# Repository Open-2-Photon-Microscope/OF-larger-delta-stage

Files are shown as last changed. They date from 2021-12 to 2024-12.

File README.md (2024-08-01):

# Substage Sample Manipulator

---
### A substitute for a micromanipulator

Our design is a modification of [Open Flexure's Delta Stage model](https://openflexure.org/projects/deltastage/) combined with a 3-axis controller box. 
The delta stage is a reliable and useful way of manipulating a small sample in X, Y and Z axes without having to move the optics of the microscope, as most current setups do.

Our aim is to use it to replace expensive hardware like [Sutter's MP-285](https://www.sutter.com/MICROMANIPULATION/mp285_frame.html), which costs a lot and effectively has to hold and manipulate the entire microscope in midair.
The setup we detail is applicable to small, low-weight samples. 
    _For larger animals such as mice, we encourage further exploration and experimentation in other projects elsewhere (but we would love know what you find before we delve in to it ourselves!!)._

This part of the project consists of two main pieces:
1. The delta stage itself, to hold and move the sample
1. [The 3-axis controller](https://github.com/Open-2-Photon-Microscope/3-axis-controller/tree/main), which uses rotary encoders to manually adjust the stage position, without the need to interface with a computer (although entirely possible).

We have made modifications to OpenFlexure's original design to allow compatability with a thorlabs cage-based substage light-collection path you can find elsewhere in the Open-2-Photon-Microscope GitHub.
Since we adjusted the scale and a few other things in the design, and since the release paper does not provide data, we have been testing the delta stage's movement, measuring how reliably it makes the same movements in a given direction, and how robust it is to drift over time. These data can be found in the 'Movement Metrics Data' folder.

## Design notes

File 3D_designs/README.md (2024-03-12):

# 3D Designs

## Optics
 - 3D printable thorlabs-compatible holders for lenses / mirrors

## STL
 - All current stl files for 3D printing:
### Centering:
1. centering card - a flat sheet with a raised hole. Slots over thorlabs cage parts held to Delta Stage. Used in conjucntion with centering top stage.
2. centering top stage - interchangable top stage with a hole for aligning with centering card

### Delta Stage for 2P
- Current working version of the Delta Stage
- large enough to contain thorlabs cage and lens (d=2in)

### Spirit Level
- Essential stage top for attaching a spirit level [url]

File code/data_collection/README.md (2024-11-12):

# Image Capture Protocol for XY Drift Analysis:

The files in this folder pertain to using a USB microscope with the [3-axis controller]() and [OF-larger delta stage](https://github.com/Open-2-Photon-Microscope/OF-larger-delta-stage)In the [`/code/`](https://github.com/Open-2-Photon-Microscope/OF-larger-delta-stage/tree/main/code) folder is a pipeline for analysing .tiff files that are derived from 2-photon microscopy files, however modified versions are named with the prefix 'jpeg' since the images they deal with (still tiff format) originate as jpeg files from the microscope. These files are the ones that will be used below but are dependent on other files in the folder. The protocol they use pertains only to X and Y drift.

## Collecting the Data  

The requires an up-to-date model of the 3-axis controller, and a way of holding the microscope above the sample (anything with distinct features so that movement can be measured).  

1. Download the files from this [folder](https://github.com/Open-2-Photon-Microscope/OF-larger-delta-stage/tree/main/code/data_collection)
2. Ensure the sample is visible from the camera (e.g. with cheese)
3. Ensure the stage is at `[0, 0, 0]` 
4. Running collect_data.py will prompt user to select the folder into which `/drift_data_x/` and all images will be saved (where x is the number of of the iteration)
	1. _NB: This is currently not true, I designed this to get the job done on my computer and it doesn't yet generalise so nicely_
5. The user is then prompted to input the number of iterations. 
	- Each iteration will take images at 9 positions (a 3x3 grid  from `[-4500,-4500]` to `[4500, 4500]`). Images will be taken at 10-minute intervals for two hours (for a total of 13 images including T0).
	- Each iteration creates its own folder
	- The number and length of the intervals the images are taken in may be modified to suit users needs'
	- Choosing many iterations allows autonomous data collection that may run for days

## When it ends  

Once the script is finished running, it will have created many folders. I recommend moving these folders to their own single folder with a clear label and date before running the script again, which would otherwise overwrite them.

## Troubleshooting  

Sometimes trouble happens: _c'est la vie_.  

- The most common error that might happen is:
	`[ WARN:0@3839.300] global cap_v4l.cpp:889 requestBuffers VIDEOIO(V4L2:/dev/video0): failed VIDIOC_REQBUFS: errno=19 (No such device)`  
	At this point the script _should_ automatically stop.
	- __Solution__: 
		1. Unplug and replug the usb microscope
		2. If the terminal is still active run `usb.moveto([0,0,0])` otherwise you will need to re-home the device manually
		3. All iterations / counting will start from 0 again so make sure to move or rename collected data so it is not overwritten

 - Sometimes an error will be in relation to the microcontroller.
	 - __Solution__: 
		 1. close all other programs that relate to the controller (including exit() from the script execution)
		 2. if that doesn't work, try unplugging the controller and turning off the power and plugging it back in (make sure to cross your fingers for good luck)

---
# Analysis Protocol:

#TODO: update this part of the protocol

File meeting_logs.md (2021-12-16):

# Meeting logs (development chat)

### 16/12/2021

Andre and Filip:

Next steps:
- setup full Open Flexure Software environment
 - Sangaboard + RPi
- Check how well it plays with [ScanImage](https://docs.scanimage.org/)
- Figure out a way to control it manually (manipulator or joystick)
- Eventually check if this also works with other software

- research open source manipulators/joysticks to control the substage system
 - if there is nothing available create something.

- find an analogue voltmeter (possible good candidate https://uk.rs-online.com/web/p/multimeters/8105526)

Outcomes from previous work package:
- Open flexure positioning is stable for our application.
- We used Serial commands over the Arduino IDE to quickly check things.

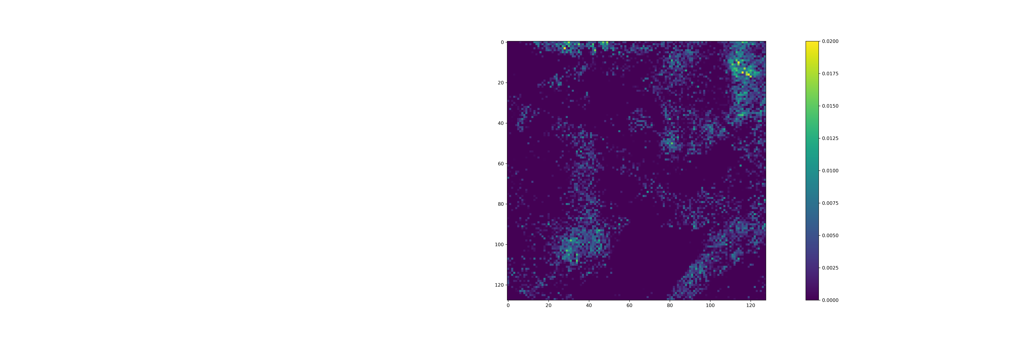
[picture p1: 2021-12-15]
media/between_recording.png

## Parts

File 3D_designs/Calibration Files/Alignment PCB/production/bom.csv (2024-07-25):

Designator | Footprint | Quantity | Value | LCSC Part #
D1, D2, D3, D4 | LED_D3.0mm | 4 | LED 2V 20mA
J1 | JST_XH_B2B-XH-A_1x02_P2.50mm_Vertical | 1 | Conn_01x02_Socket
R1, R2 | R_Axial_DIN0207_L6.3mm_D2.5mm_P7.62mm_Horizontal | 2 | 51

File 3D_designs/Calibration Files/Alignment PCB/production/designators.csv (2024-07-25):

D1:1
D2:1
D3:1
D4:1
J1:1
R1:1
R2:1

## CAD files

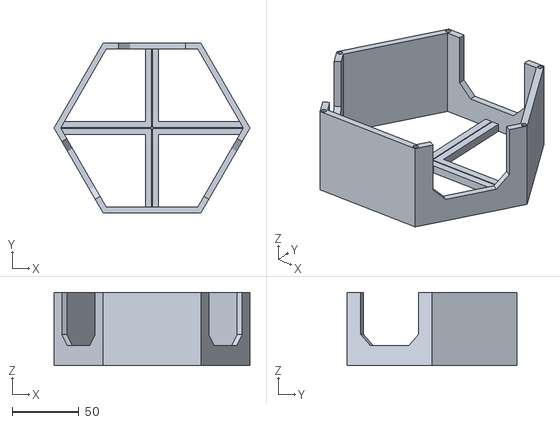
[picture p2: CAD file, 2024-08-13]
3D_designs/Calibration Files/stage_calibration_0_5.stl
147.0 x 127.3 x 55.0

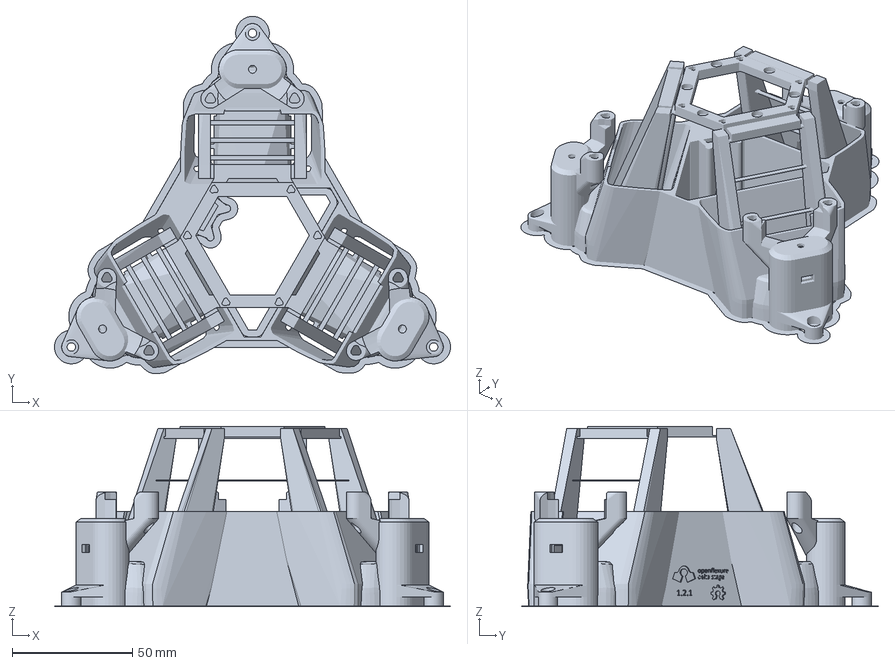
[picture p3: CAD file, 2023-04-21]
3D_designs/delta_stage_with_stage_mount_holes.3mf
164.7 x 148.5 x 75.0 mm

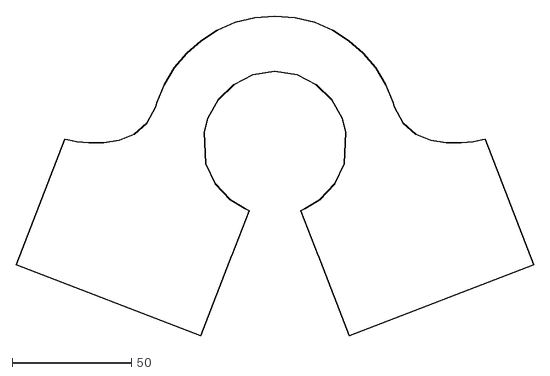
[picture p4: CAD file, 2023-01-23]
3D_designs/open_flexure_delta_copy_20230123/openflexure-microscope/openscad/openflexure_emblem.dxf
216.7 x 134.0

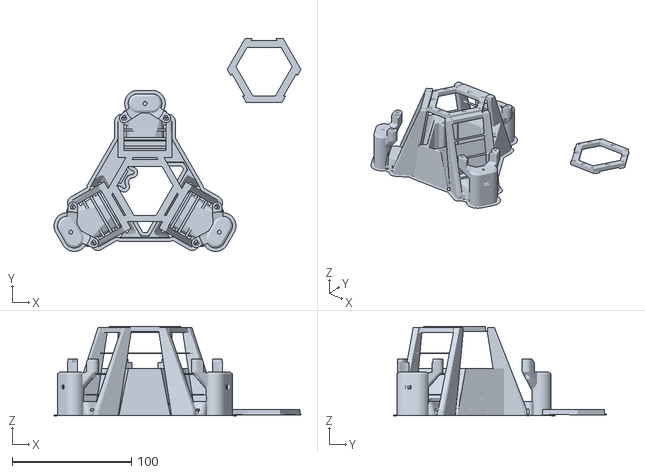
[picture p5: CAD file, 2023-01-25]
3D_designs/open_flexure_delta_copy_20230123/openscad/both.stl
207.4 x 178.8 x 75.0

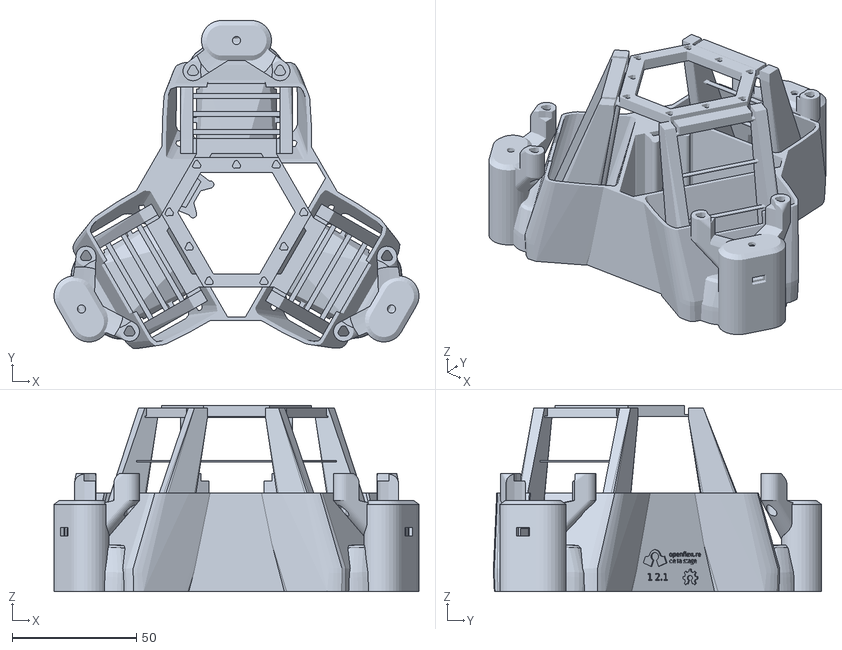
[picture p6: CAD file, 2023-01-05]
3D_designs/sample_holders/delta_stage.stl
146.8 x 132.0 x 75.0

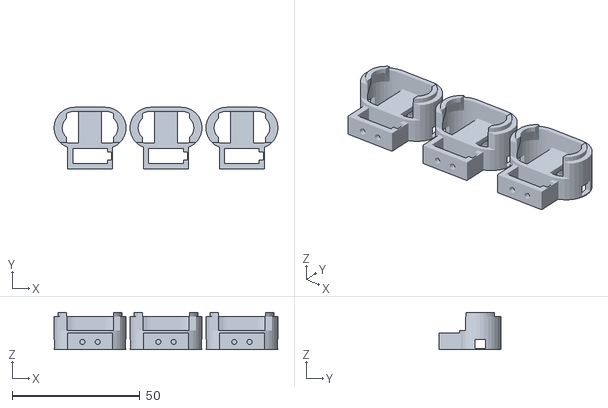
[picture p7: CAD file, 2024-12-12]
3D_designs/STL/feet_with_endstop.stl
87.6 x 24.1 x 14.5

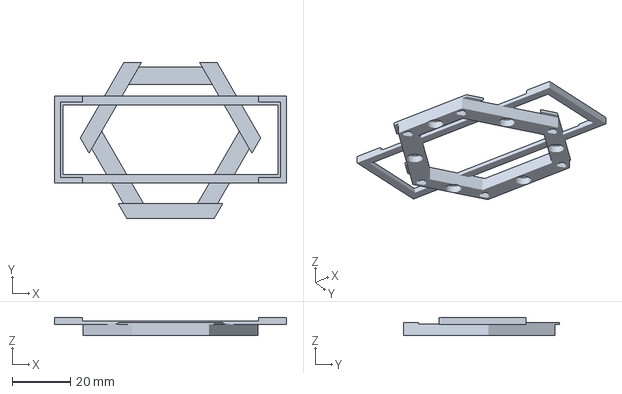
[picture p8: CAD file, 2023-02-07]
3D_designs/microscope_slide_holder.3mf
79.7 x 53.7 x 6.20 mm

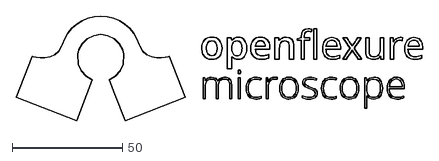
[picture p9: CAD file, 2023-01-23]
3D_designs/open_flexure_delta_copy_20230123/openflexure-microscope/openscad/openflexure_logo.dxf
184.0 x 47.3

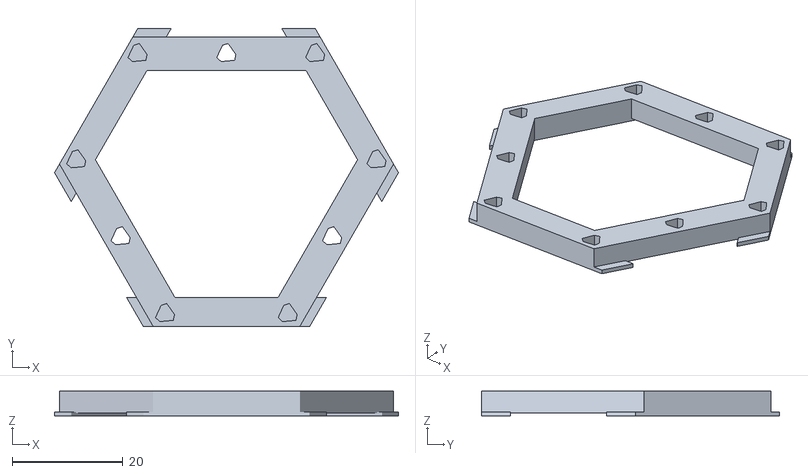
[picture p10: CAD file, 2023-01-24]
3D_designs/open_flexure_delta_copy_20230123/openscad/adapter.stl
62.0 x 53.7 x 4.50

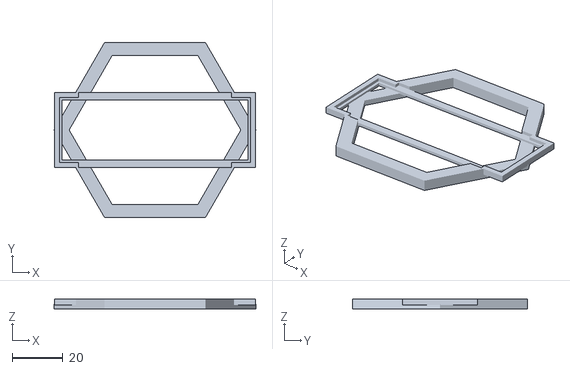
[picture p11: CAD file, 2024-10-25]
3D_designs/STL/top_stage_lower.stl
80.0 x 69.3 x 4.00

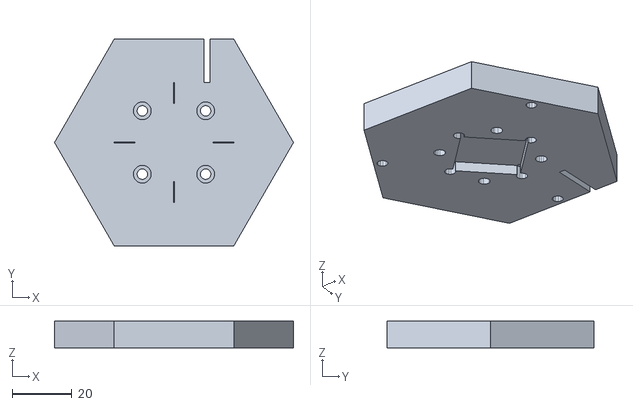
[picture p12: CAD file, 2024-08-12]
3D_designs/Calibration Files/stage_calibration_top_v2.stl
80.0 x 69.3 x 9.00

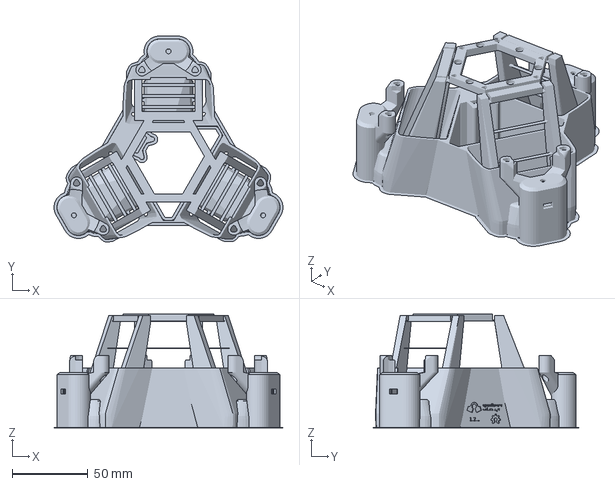
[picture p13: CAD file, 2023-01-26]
3D_designs/delta_stage.3mf
150.8 x 135.6 x 75.0 mm

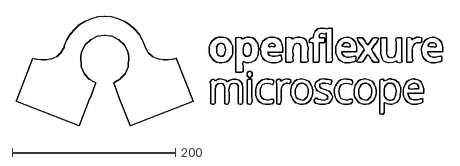
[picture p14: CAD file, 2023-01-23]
3D_designs/open_flexure_delta_copy_20230123/openflexure-microscope/openscad/openflexure_logo_outset.dxf
524.2 x 134.0

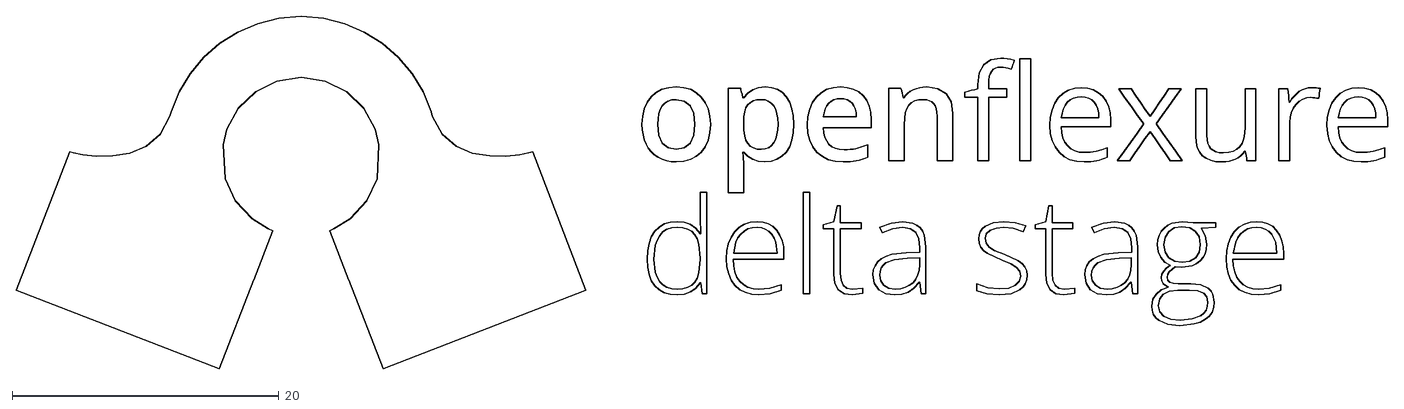
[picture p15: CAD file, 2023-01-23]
3D_designs/open_flexure_delta_copy_20230123/openscad/openflexure_delta_stage_logo.dxf
102.8 x 26.4

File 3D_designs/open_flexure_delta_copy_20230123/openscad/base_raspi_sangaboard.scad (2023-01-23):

include <parameters.scad> //Delta-stage params
use <../openflexure-microscope/openscad/utilities.scad>;
use <../openflexure-microscope/openscad/compact_nut_seat.scad>;
use <delta_stage.scad>
use <delta_stage_logo.scad>;
use <../openflexure-microscope/openscad/logo.scad>;

module base_projection(){
    projection(cut=true){
        union(){
            difference(){
                union(){    // casing around the leg&lever
                    each_lever() minkowski(){
                        leg_and_lever_clearance();
                        cylinder(r1=wall_t, r2=0.5, h=0.9);
                    }
                    reflect([1,0,0]){
                        translate([-(casing_radius+1),0,0])cube([(casing_radius+1),casing_apothem,10]); // This fills in space in the side that are then later cut to give access to side RPi connections.
                    }
                }
                translate([0,sangaboard_center[1]-sangaboard[1]/2,0])cube([100,sangaboard[1],10]); // This squares off the side wall for access to Sangaboard connections
                translate([-(casing_radius+1),2.5,0])cube([(casing_radius+1),casing_apothem,10]); // This squares off the side wall for access to RPi connections
                translate(raspi_center+[0,-(raspi_board[1]+2),-raspi_standoff])cube(raspi_board+[10,0,0],center=true); //This squares off the back wall for access to RPi connections
            }
            // This fills in where the RPi goes with extra space at the front of the microscope as the Sangaboard is bigger that the RPi in that dimension
            translate(raspi_center-[0,-2,raspi_standoff]) cube(raspi_board + [1,8,0], center =true);
        }
    }
}

module feet_projection() {
    projection(cut=true){
        // casing for the actuator
        each_lever() translate([0, nut_y, -49]) screw_seat_shell(h=actuator_h + 99);
    }  
}

module base_extrusion(h) {
    linear_extrude(height=h) {
        union() {
            feet_projection();
            base_projection();
        }
    }
}

module base_hollow(cutout_tolerance=1) {
    difference(){
        union(){
        // Base extrusion, but with an outer wall wall_thickness thick
            minkowski(){
                base_extrusion(base_height);
                cylinder(r=wall_thickness+cutout_tolerance,h=1);
            }
            stage_connection();
        }
        // Base extrusion, but with an outer wall cutout_tolerance thick
        translate([0, 0, wall_thickness]) minkowski(){
            base_extrusion(base_height);
            cylinder(r=cutout_tolerance,h=1);
        }
    }
}

module foot_stands(height=base_height, cutout_tolerance=1) {
    // Creates 3 ledges approximately half the foot size such that the main body of the microscope will start 2mm below the height of the base.
    translate([0,0,height-foot_height+1]){
        each_lever(){
            translate([0, nut_y, 0]){
                intersection(){ 
                    hull(){
                        difference(){
                            minkowski(){
                                linear_extrude(d){
                                    projection(){
                                        screw_seat_shell(10);
                                    }
                                }
                                cylinder(r=cutout_tolerance,h=d);
                            }
                            translate([0,-52.5,0])cube([100,100,100],center = true);
                        }
                        translate([0,10,-20]) cube([30,d,d],center=true);
                    }
                    translate([0,0,-50]){
                        minkowski(){
                            screw_seat_shell(100);
                            cylinder(r=cutout_tolerance+1,h=d);
                        }
                    }
                }
            }
        }    
    }
}

//The walls and floor of the base
module base() {
    union(){
        foot_stands(cutout_tolerance=base_cutout_tolerance);
        base_hollow(cutout_tolerance=base_cutout_tolerance);
    }
}

// All the windows to pass cables through
module window_cubes() {
    //RPi windows
    // Back window
    translate(raspi_center+[0,-50,-raspi_board[2]/2+USB_ethernet_window[2]/2-3]) cube(USB_ethernet_window,center=true);

    //Side window
    translate(raspi_center+[-power_HDMI_window[0]/2,raspi_board[1]/2-power_HDMI_window[1]/2-3.5,-raspi_board[2]/2+power_HDMI_window[2]/2-1]) cube(power_HDMI_window,center = true);
    
    //Vents
    translate([sangaboard_center[0]+50,sangaboard_center[1]+5/2,raspi_center[2]])repeat(delta=[0,(sangaboard[1]-5)/14,0],N=15, center= true) cube([100,1.5,power_HDMI_window[2]],center=true);

    //SD card access
    translate(raspi_center+[0,raspi_board[1]/2+5,-10])cube([20,25,20], center=true);


    //Sangaboard windows
    // Back window
    translate(sangaboard_center-[0,50,0]) rotate([0,0,90])cube(sangaboard_window, center=true);

    //Side windows
    translate([raspi_center[0]-power_HDMI_window[0]/2,raspi_center[1]+raspi_board[1]/2-power_HDMI_window[1]/2-3.5,sangaboard_center[2]-sangaboard[2]/2+power_HDMI_window[2]/2+3]) cube(power_HDMI_window+[0,0,6], center = true);
    translate(sangaboard_center+[50,5/2,-sangaboard[2]/2+power_HDMI_window[2]/2+3]) cube([100,sangaboard[1]-5,power_HDMI_window[2]+6],center = true);
    //Reflection gap
    rotate([0,0,-60])translate([0,50,base_height-9])cube([bottom_cutout_w,100,20],center=true);
}

module pi_supports(){
    // position supports for each of the pi's mounting screws
    translate(raspi_center+[0,raspi_center[1],-raspi_center[2]]) repeat([49,0,0],2, center=true) repeat([0,58,0], 2,center=true) children();
}

// The four mounting holes underneath the Raspberry Pi.  
module raspi_supports(){
    difference(){
        pi_supports() cylinder(h=raspi_standoff, d=7);
        pi_supports() trylinder_selftap(2.5, h=999, center=true);
    }
}

module stage_connection(height=base_height){
    // Creates 3 mounting posts to connect to the main body. The top of the post is in line with the top of the base, with the cutout circle 2mm down such that the main body sits 2mm under the top of the base.
    translate([0,0,height+1])
    {
        each_base_mounting_point(){
            difference(){
                hull(){
                    translate([0,0,-2*d])repeat([0,0,-10],2){
                        minkowski(){
                            cube([10,10,d], center = true);
                            cylinder(r = 1, h = d, $fn = 50);
                        }
                    }
                    translate([0,nut_y+stage_r-mounting_point,-20]){
                        difference(){                                
                            linear_extrude(20){
                                projection(){
                                    minkowski(){
                                        screw_seat_shell(10);
                                        cylinder(r=wall_thickness,h=d);
                                    }
                                }
                            }
                        translate([-50,-99,-50])cube([100,100,100]);
                        }
                    }
                }
                translate([0,0,-2])cylinder(d = 8.5, h = 2, $fn=50);
                translate([0,0,-8+d])cylinder(d= 3.5, h = 8, $fn=50);
                translate([0,0,-10-8+d])trylinder_selftap(3, h=20, center=true);
                hull()repeat([0,100,0],2) translate([0,0,-8]) cylinder(d=6.9,h=2.8,$fn=6); 
            }
        }
    }
}

// Used to show position of sangaboard
module sangaboard(){
    translate(sangaboard_center) cube(sangaboard, center =true);
}

//Used to show position of raspberry pi
module raspi(){
    translate(raspi_center)cube(raspi_board, center = true);
}

module logos(){
    //The OSHW and OpenFlexure logos (goes on back of the base)
    rotate(-90)translate([casing_apothem-3.5,8,base_height*0.7])rotate([90,0,-90])scale([0.2,0.2,1])oshw_logo_and_text(version_numstring);
    mirror([1,0,0])rotate(-90)translate([casing_apothem-3.5,4,base_height*0.8])rotate([90,0,-90])scale([0.2,0.2,1])openflexure_delta_stage_logo();
}

module base_windowed() {
    union(){
        difference() {
            base();
            window_cubes();
            translate([-(casing_radius+2),0,base_height-5])cube([casing_radius+2,sangaboard_center[1]+sangaboard[1]/2-sangaboard_window[1]/2,10]); // cutout at top for the base to pass under the mircoscope (side)
            translate([0,sangaboard_center[1]-sangaboard[1]/2,base_height-5])cube([100,sangaboard[1]/2,10]); // cutout at top for the base to pass under the mircoscope (side)
            translate(raspi_center+[0,-(raspi_board[1]+2),base_height-5-raspi_standoff])cube(raspi_board+[10,0,0],center=true); //cutout at top for the base to pass under the mircoscope (back)
            logos();
        }
        raspi_supports();
    }
}
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

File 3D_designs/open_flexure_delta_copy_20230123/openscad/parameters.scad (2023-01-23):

/*
  Useful settings/parameters for the OpenFlexure fibre stage
*/

use <../openflexure-microscope/openscad/reflection_illuminator.scad>;
version_numstring = "1.2.1"; 

// Set the overall geometry
leg_strut_l = 32; // inner width of the legs
stage_r = 25; // distance from the centre to the edge of the stage
flex_z1 = 0; // height of lower flexures
flex_z2 = 70; // height of upper flexures

// Thickness of legs
leg_t = 5;

// Set the length of the actuating levers
xy_gain = 2; // ratio of stage motion to Z motion
lever_l = (flex_z2 - flex_z1)/xy_gain;
nut_y = lever_l + 12;

// Motor lugs
motor_lugs = true;

// Condenser mount
transmission_illumination = false;

// Reflection illumination - The hole cut out the side for the reflection illuminator
reflection_illumination = false; 

// Stage connectors - the mounts to connect the stage to the base
stage_connectors = false;

//Objective mount - the dovetail for attaching the optics module
optics_module_mount = true;

// Flexure dimensions - good for PLA and ~0.5mm nozzle
zflex = [6, 1.5, 0.75]; //dimensions of flexure
flex_a = 0.1; //angle through which flexures are bent, radians
dz = 0.5; //thickness before a bridge is printable-on

actuator_h = 30; //height of actuator columns (~screw length)
actuator_travel = (nut_y - zflex[1]/2)*flex_a;

wall_t = 1.6;
d=0.05;

// Mounting stuff
// Mounting holes should be 60 degrees out from the legs (i.e. in between)
// If you extend the line of the solid anchor part in the middle (where each leg
// joins the casing) out sideways, to the middle of the vertical part of the
// leg, then take the midpoint of the line joining each pair, that's the hole)
mounting_hole_r = sin(30)*stage_r + sin(60)*(leg_strut_l/2+zflex[1]+leg_t/2);
// The position of the mounting point between the base and main body (from centre at each 120 degree position of the actuators)
mounting_point = 87;

// Objective mount
objective_mount_y = 18; // y position of clip for optics
objective_mount_back_y = stage_r + wall_t; //back of objective mount
objective_mount_nose_w = 6; // width of the pointy end of the mount

sample_z = 65; // height of the top of the stage
z_flexures_z1 = 8; // height of the lower Z flexure
z_flexures_z2 = min(sample_z - 12, 35); // " upper "

// Feet
feet_endstops = false;
foot_height=feet_endstops?15:15; //the endstops need a bit of extra height (or not)
endstop_extra_ringheight=feet_endstops?1:0;

//Casing 
casing_height = actuator_h+actuator_travel + 5; //flex_z2-24; //the maximum height of the lever casing and 'joining together' casing
casing_radius = nut_y; //the outside radius (to the point) of the hexagon used to join the casing together

// size of cutout for fl cube
top_cutout_w = stage_r/2 + 2*wall_t; // As big as we can get at height 'wall_h' without bridging a corner
mid_cutout_w = illuminator_width() + 1;
bottom_cutout_w = illuminator_width() + 4;

// Base
wall_thickness = 2;
simple_base_height = 35;
base_height = 80;
base_cutout_tolerance = 0.5;
raspi_board = [56,85,16]; // The actual size of the RPi
casing_apothem = casing_radius*sqrt(3)/2; // The apothem of the hexagon used to join up the legs
USB_ethernet_window = [raspi_board[0],100,raspi_board[2]+6]; //The back window for the RPi
power_HDMI_window  = [100,45-3.5,14]; //The side window for the RPi
raspi_standoff = 7; //How high the RPi is from the base (governed by the standoff screw size)
sangaboard = [56,68,25]; // The actual size of the Sangaboard
raspi_center = [0,10,raspi_board[2]/2+raspi_standoff]; // Where the centre of the Raspberry Pi is in its final position
standoff_height = 20; //The height of the standoff between the Rpi and the Sangaboard
sangaboard_center = raspi_center+[0,(raspi_board[1]/2-sangaboard[1]/2),(sangaboard[2]/2-raspi_board[2]/2+standoff_height)]; // Where the centre of the Raspberry Pi is in its final position
sangaboard_window = [100,power_HDMI_window[1],20]; // The back window of Sangaboard

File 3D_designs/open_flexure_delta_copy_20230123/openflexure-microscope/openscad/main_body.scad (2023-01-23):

/******************************************************************
*                                                                 *
* OpenFlexure Microscope: Microscope body                         *
*                                                                 *
* This is the chassis of the OpenFlexure microscope, an open      *
* microscope and 3-axis translation stage.  It gets really good   *
* precision over a ~10mm range, by using plastic flexure          *
* mechanisms.                                                     *
*                                                                 *
* (c) Richard Bowman, January 2016                                *
* Released under the CERN Open Hardware License                   *
*                                                                 *
******************************************************************/

use <./utilities.scad>;
use <./compact_nut_seat.scad>;
use <./logo.scad>;
use <./dovetail.scad>;
use <./z_axis.scad>;
use <./gears.scad>;
use <./wall.scad>;
use <./main_body_transforms.scad>;
use <./reflection_illuminator.scad>;
include <./microscope_parameters.scad>; //All the geometric variables are now in here.


module leg(brace=stage_flex_w){
    // The legs support the stage - this is either used directly
    // or via "actuator" to make the legs with levers
    fw=stage_flex_w;
	union(){
       	//leg
		reflect([1,0,0]){
			//vertical legs
			translate([leg_middle_w/2+zflex_l,0,0]) hull(){
				cube(leg);
				cube([leg[0],fw+brace,d]); //extend it to be a triangle
			}

            //flexure bridges between the legs
            zs = [flex_z1, flex_z2]; //heights of bridges between legs
            bs = [brace, 0]; //"brace positions" - a nonzero value here
                             //widens the leg, and adds another flexure
                             //at the new position.  bs[i]=fw will double
                             //the width of the flexure, while a larger 
                             //value produces two distinct flexures.
			for(i=[0,1]) translate([0,0,zs[i]]){
				translate([-d,0,0]) hull() repeat([0,bs[i],0],2) //solid part
                        cube([leg_middle_w/2+d,leg[1],stage_t-0.2*leg[1]]);
				translate([-d,0,0]) repeat([0,bs[i],0],2) //flexures
                        cube([leg_middle_w/2+zflex_l+leg[0],leg[1],zflex_t]);
			}
		}
        
		//thin links between legs
		if(flex_z2-flex_z1 > 2*bridge_dz){
			n=floor((flex_z2-flex_z1)/bridge_dz);
			dz=(flex_z2-flex_z1)/n;
			translate([0,leg[1]/2,flex_z1+dz]) repeat([0,0,dz],n-1) cube([leg_outer_w,2,0.5],center=true);
		}
	}
}
module actuator(){
    // A leg that supports the stage, plus a lever to tilt it.
    // No longer includes the flexible nut seat actuating column.
    // TODO: find the code that unifies this with leg()
	brace=20;
    fw=stage_flex_w;
    w = actuator[0];
    union(){
        leg(brace=brace);

		//arm (horizontal bit)
		difference(){
            sequential_hull(){
                translate([-leg_middle_w/2,0,0]) cube([leg_middle_w,brace+fw,4]);
                translate([-w/2,0,0]) cube([w,brace+fw+0,actuator[2]]);
                translate([-w/2,0,0]) cube(actuator);
            }
            //don't foul the actuator column
            translate([0,actuating_nut_r,0]) actuator_end_cutout(); 
        }

	}
}
module actuator_silhouette(h=999){
    // This defines the cut-out from the base structure for the XY
    // actuators.
    linear_extrude(2*h,center=true) minkowski(){
        circle(r=zflex_l,$fn=12);
        projection() actuator();
    }
}

module back_foot_mounting_screw(d=3*0.95, h=16, center=true){
    translate([0,illumination_clip_y+3,0]) cylinder(d=d, h=h,center=center);
}

module mounting_hole_lugs(){
    // lugs either side of the XY table to bolt the microscope down
    //these are to mount onto the baseplate 
    for(p=base_mounting_holes) {
        if(p[1]<0 && p[0]>0) reflect([1,0,0]) hull(){
            translate([z_flexure_x,0,0]) rotate(-120) cube([10,d,10]);
            translate(p) cylinder(r=4*1.1,h=3);
        }
    }
}

module xy_limit_switch_mount(d=3.3*2, h=6){
    // A mount for the XY limit switch (M3)
    leg_frame(45) translate([-9, -zflex_l-zawall_h*sin(6)-3.3+1, zawall_h-6]) cylinder(d=d,h=h);
}


// The "wall" that forms most of the microscope's structure
module wall_inside_xy_stage(beamsplitter=false){
    front_wall_height = beamsplitter ? zawall_h : wall_h;
    // First, go around the inside of the legs, under the stage.
    // This starts at the Z nut seat.  I've split it into two
    // blocks, because the shape is not convex so the base
    // would be bigger than the walls otherwise.
    reflect([1,0,0]) sequential_hull(){
        //inner_wall_vertex(-45, -leg_outer_w/2-wall_t/2, zbwall_h);
        mirror([1,0,0]) z_bridge_wall_vertex();
        z_bridge_wall_vertex();
        inner_wall_vertex(45, -leg_outer_w/2, zawall_h);
        z_anchor_wall_vertex();
        inner_wall_vertex(135, leg_outer_w/2, zawall_h);
        inner_wall_vertex(135, -leg_outer_w/2, front_wall_height);
        inner_wall_vertex(-135, leg_outer_w/2, front_wall_height);
    };    

}

module wall_outside_xy_actuators(){
    // Add the wall from the XY actuator column to the middle
    sequential_hull(){
        z_anchor_wall_vertex(); // join at the Z anchor 
        // [nb this is no longer actually the z anchor since the new z axis]
        // anchor at the same angle on the actuator
        // NB the base of the wall is outside the
        // base of the screw seat
        leg_frame(45) translate([-ss_outer()[0]/2+wall_t/2,actuating_nut_r,0]){
            rotate(-45) wall_vertex(y_tilt=atan(wall_t/zawall_h));
        }
    }
}

module wall_inside_xy_actuators(){
    // Connect the Z anchor to the XY actuators
    hull(){
        translate([-(z_anchor_w/2+wall_t/2+1), z_anchor_y + 1, 0]) 
                     wall_vertex();
        y_actuator_wall_vertex();
    }
}

module wall_between_actuators(){
    // link the actuators together
    hull(){
        y_actuator_wall_vertex();
        translate([0,z_nut_y+ss_outer()[1]/2-wall_t/2,0]) wall_vertex();
    }
}

// Cut out hole for reflection illuminator
module fl_cube_cutout(){
    // size of cutout for fl cube
    top_cutout_w = 17.8; // As big as we can get at height 'wall_h' without bridging a corner
    mid_cutout_w = illuminator_width() + 1;
    bottom_cutout_w = illuminator_width() + 4;

    // Create a trapezoid with min width (cube_width) at top
    hull() {
        translate([-(bottom_cutout_w)/2, -49, -0.5]) cube([bottom_cutout_w, 49, 1]);
        translate([-(mid_cutout_w)/2, -49, 10]) cube([mid_cutout_w, 49, 1]); // Highest we usually need
        translate([-top_cutout_w/2, -49, wall_h]) cube([top_cutout_w, 49, 1]);
    }
}

///////////////////// MAIN STRUCTURE STARTS HERE ///////////////
module main_body(){
    // This module represents the main body of the microscope, including the positioning mechanism.

	//legs (incl. actuators)
	reflect([1,0,0]) leg_frame(135) leg();
	each_actuator(){
        actuator();
		translate([0,actuating_nut_r,0]) actuator_column(h=actuator_h, join_to_casing=true);
    }
	//flexures connecting bottoms of legs to centre
	each_leg() reflect([1,0,0]) translate([0,0,flex_z1]){
        w=stage_flex_w;
        translate([leg_middle_w/2-w,0,0.5]) hull()
			repeat([1,-1,0]*(zflex_l+wall_t/2),2) cube([w,d,zflex_t]);
    }
    //tie the legs to the wall (built later) during printing
    reflect([1,0,0]) leg_frame(135) reflect([1,0,0]) {
        translate([leg_middle_w/2+zflex[1]+zflex[0]/2, -wall_h*0.7*tan(6)-1-zflex[1], wall_h*0.7]) cube([1, wall_h*0.7*tan(6)+2+zflex[1], 0.5]);
    }

	// flexures between legs and stage
    // NB these connect the legs together, and pass all the way under the stage.  This
    // is important, if they get cut then the bridges will fail!
	difference(){
		hull() each_leg() translate([0,0,flex_z2+zflex_t/2+0.5]) cube([leg_middle_w,d,zflex_t],center=true);
		hull() each_leg() cube([leg_middle_w-2*stage_flex_w,d,999],center=true);
	}
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

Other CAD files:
3D_designs/Calibration Files/stage_calibration.stl
3D_designs/STL/top_stage_egg.stl
3D_designs/open_flexure_delta_copy_20230123/openflexure-microscope/openscad/oshw_gear.dxf
3D_designs/open_flexure_delta_copy_20230123/openscad/delta_stage.stl
3D_designs/open_flexure_delta_copy_20230123/openflexure-microscope/openscad/main_body_transforms.scad
3D_designs/STL/centering_card.stl
3D_designs/STL/centering_top_stage.stl
3D_designs/STL/delta_stage_for_2p.stl
3D_designs/STL/legacy_unused_files/centering_card.stl
3D_designs/STL/legacy_unused_files/centering_top_stage.stl
3D_designs/STL/legacy_unused_files/delta_stage.scad
3D_designs/STL/legacy_unused_files/delta_stage_head.scad
3D_designs/STL/legacy_unused_files/sample_holders/holders.scad
3D_designs/STL/top_stage_egg_1.stl
3D_designs/STL/top_stage_offset.stl
3D_designs/STL/top_stage_offset_2.stl
3D_designs/STL/top_stage_slide_holder.stl
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

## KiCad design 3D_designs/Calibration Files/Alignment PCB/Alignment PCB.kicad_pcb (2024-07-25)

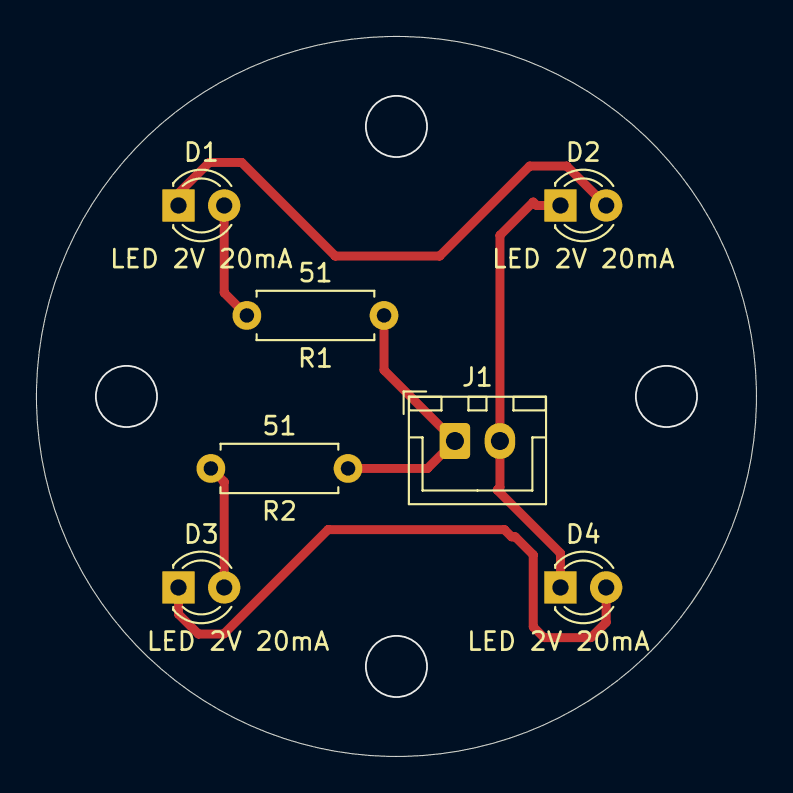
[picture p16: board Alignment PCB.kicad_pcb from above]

Board: 2 copper layers, 40.0 x 40.0 mm, 7 parts (0 on the bottom side), 6 nets.

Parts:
D1, D2, D3, D4: LED 2V 20mA; LED_D3.0mm
J1: Conn_01x02_Socket; JST_XH_B2B-XH-A_1x02_P2.50mm_Vertical
R1, R2: 51; R_Axial_DIN0207_L6.3mm_D2.5mm_P7.62mm_Horizontal

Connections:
+5V: J1.1, R1.1, R2.1
GND: D2.1 (K), D4.1 (K), J1.2
unnamed: D1.2 (A), R1.2
unnamed: D1.1 (K), D2.2 (A)
unnamed: D3.2 (A), R2.2
unnamed: D3.1 (K), D4.2 (A)

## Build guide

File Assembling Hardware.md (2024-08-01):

## Part 1: Assembling Hardware
### 1.1 Delta Stage  
*This is the part that will be holding the sample.*

1. To get started, download our [custom body stl file from github](https://github.com/Open-2-Photon-Microscope/substage/tree/main/3D_designs) and print it out.  
  
1. Follow instructions on [this page](https://build.openflexure.org/openflexure-delta-stage/v1.2.2/pages/index_transmission/pages/assembling_the_actuators.html) - substituting the [main body]() for the one you just printed.
    * *Make sure motors A, B and C are positioned clockwise from above, otherwise movement will be inverted.*  
  
1. Download and print:
    1. a [sample holder](https://github.com/Open-2-Photon-Microscope/substage/tree/main/3D_designs/sample_holders) that will suit your needs.
    1. a [calibration tool and stage-top](https://github.com/Open-2-Photon-Microscope/OF-larger-delta-stage/tree/main/3D_designs/Calibration%20Files)

1. Carefully glue fifteen 3x2 magnets into the stage.
    1. Three in the top of the stage itself
    1. Three in the sample holder
    1. Three more in the stage-top calibration part
        __MAKE SURE THESE SETS MATCH POLARITY__
    1. Three round the perimiter to attach to the calibration tool
    1. Three round the base of the calibration tool
        __Again, make sure these two sets match!!__
    
[figure_showing correct_motor_configuration]  
If your stage looks like this: congratulations! Keep going to the next steps!

### 1.2 Controller Box
*This holds the electronics and dials you will use to control the stage.*

1. Download and print the files of the [3D printed case](https://github.com/Open-2-Photon-Microscope/3-axis-controller/tree/main/box%20design/stl).  
  
1. Use __m3 screws and nuts__ to attach the [custom driver board](https://github.com/Open-2-Photon-Microscope/3-axis-controller/tree/main/electronics%2Fintegrated_board) to bottom of case.
[figure_of_boards_on_case_highlight_screws]  
  
1. Attach the [ENA1J-B28-L00100L optical encoders](https://uk.farnell.com/bourns/ena1j-b28-l00100l/encoder-rotary-optical-300rpm/dp/2321812) to the front part of the case.  
  
1. Use __JST XH-4 cables__ to attach the optical encoders to the board.
    * *Make sure to plug the correct encoder into its corresponding axis port on the board (XYZ).*   
[figure_of_encoder_plugged_in_correctly]  
  
1. Use a long ribbon cable to attach the motors to the board.
    * *This cable is 3-in-1 so be sure the ends you are using correspond to the correct motor ports on the board (ABC) and have been assembled correctly.*  
[figure_of_ribbon_cable_labelled]  
  
1. Assemble the rest of the case around the boards and cables.
    * *Make sure the 12V power supply and micro USB cable can plug in through the holes!!!*  
  
[figure_of_assembled_box_and_stage]  
You're all done with hardware! Look at you go!

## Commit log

2021-10-25 clean up and rename 3d designs, plus add licenses on all files
    [big_lens_holder.scad, condenser.scad, small_lens_holder.scad, xy_mirror.scad]
2023-01-05 start working on adapter for slide holders
    [delta_stage.stl]
2023-01-23 start start working on the adapter
    [10mm_riser.scad, 1_inch_disc_holder.scad, 35mm_petri_dish_holder.scad, 55mm_petri_dish_holder.scad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]
2023-01-23 remove doc files from openflexure delta stage to decrease repo size
2023-01-24 reorganise repos
    [big_lens_holder.scad, condenser.scad, delta_stage.stl, small_lens_holder.scad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]
2023-01-24 update adapter
    [adapter.stl, delta_stage.scad]
2023-01-25 update designs and first holder
    [both.stl, delta_stage.scad, holders.scad]
2023-01-25 update stage design
    [delta_stage.scad]
2023-01-26 reorganise repo
    [delta_stage.scad, delta_stage.stl, delta_stage_head.scad, microscope_slide_holder.3mf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]
2023-01-26 clean up build
    [delta_stage.3mf, delta_stage.scad]
2023-02-07 update desingsd
    [delta_stage_head.scad, holders.scad, microscope_slide_holder.3mf, microscope_slide_holder.amf]
2023-04-21 update 3D design
    [delta_stage.scad, delta_stage_with_stage_mount_holes.3mf]
2024-02-08 Added 2 ImageJ macros :
    - 1_Z_project_and_contrast_imageJ_macro.ijm :
    From the raw .tiff files, average the slices and tweak intensity and contrast.
    Outputs the flattened image as a .tiff in a dedicated subfolder "Z_proj" in the same directory as the input files.
    Doesn't process stacks containing the wrong number of slices (filters out faulty recordings).
    - 2_Alignment_and_drift_imageJ_macro.ijm :
    This script select the correct files for alignment according to user input ( All zeros, X displacement, Y displacement or ALL)
    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
2024-03-12 Updated delta stage and alignment designs
    + Tidied files.
    + Added updated deltastage scad and stl files.
    + Added alignment scad and stl files.
    + Added README.
    [10mm_riser.scad, 35mm_petri_dish_holder.scad, 52 square.scad, 55mm_petri_dish_holder.scad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]
2024-06-26 updating calibration top
    thinner slits for LEDs and wider holes to fit m3 screws
    general tidying
    [calibration_top.stl, centering_card.stl, centering_top_stage.stl, stage_calibration.scad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]
2024-07-15 Alignment PCB
    Created Alignment PCB
    Moved alignment/calibration STLs to Calibration Files folder
    [Alignment PCB-B_Cu.gbr, Alignment PCB-B_Mask.gbr, Alignment PCB-B_Paste.gbr, Alignment PCB-B_Silkscreen.gbr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]
2024-07-25 small updates on aligment pcb, create files for producton
    [Alignment PCB.kicad_pcb, Alignment PCB.kicad_sch, bom.csv, designators.csv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]
2024-07-25 Added magnets for calibration parts
    delta stage and calibration body now have holes for six 3x2 magnets. Maybe will remove the need for the feet on calibration body soon
    [delta_stage_for_2p.scad, delta_stage_for_2p.stl, stage_calibration.scad, stage_calibration.stl]
2024-07-26 Fixed Delta Stage Bug
    One arm of the deltastage was merged into the body somehow... now fixed
    ofds snap.scad file is a snapshot from before prior update
    [delta_stage_for_2p.stl, ofds snap.scad]
2024-08-12 modified calibration top
    There is a slit in the calibration top to allow the wire to pass from above to below without needing to be passed under the stage
    [stage_calibration.scad, stage_calibration_top_v2.stl]
2024-08-13 removed slant holes from calibration
    The alignment for the stage can be done by magnets, no need for extra connectors
    [stage_calibration.scad, stage_calibration.stl]
2024-08-13 modification to calibration top slit
    stage_calibration.scad module calibration_body now has parameter slit, which can specify thickness.
    [stage_calibration.scad, stage_calibration_0_5.stl]
2024-10-25 Added expanded designs for egg chamber
    compatability with drosophila embryo chambers
    [chamber.scad, stage_calibration.scad, top_stage.scad, top_stage_egg.stl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]
2024-10-25 lowered mic slide height
    [top_stage.scad, top_stage_lower.stl]
2024-10-25 create petri dish holder
    [top_stage.scad]
2024-12-12 Modified feet .scad
    Added slot for attaching endstop microswitch
    [feet.scad, feet_with_endstop.stl]
2025-02-27 Tidied files
    [top_stage_egg_0.stl]
